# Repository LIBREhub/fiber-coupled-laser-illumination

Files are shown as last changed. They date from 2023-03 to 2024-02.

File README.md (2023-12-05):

# Low-cost and modular fiber-coupled laser illumination for microscopy 

The modular fiber-coupled laser illumination is a free and open-source system that features lasers with various wavelengths coupled in a single optic fiber, enabling easy digital selection without any structural modifications. The system is modular, allowing individual parts to be repurposed and improved in the open-source hardware sense, and easily combined, exchanged, or used on their own.

## Usage

### Instructions

* [Assembly instructions]()
    * [Parts list]()
    * [Firmware installation]()
* Usage instructions
	* [Controller usage]()

This project is documented with GitBuilding - an OpenSource project for documenting hardware projects. For more information on the GitBuilding project, or how
to install GitBuilding please see the [GitBuilding website](http://gitbuilding.io)

## Design files and source code

* [3D printed parts]()
* [Electronics]()
* [Firmware]()

## How do I edit the documentation?

To edit the documentation you do not need to install anything, the documentation files can
be opened in a plain text editor such as Windows Notepad, Notepad++, gedit, VS Code, etc.
We recommend installing GitBuilding to preview any changes to the documentation.
GitBuilding also comes with a browser-based editor that has a live display of the final HTML documentation.

If you have ever used [markdown](https://www.markdownguide.org/basic-syntax/) you will
notice that the files you are editing are markdown files. GitBuilding uses an extended
markdown syntax (that we call BuildUp). This allows you to keep track of parts in the
documentation. More detailed documentation is available on the
[GitBuilding website](https://gitbuilding.io). There is also additional
[syntax for configuration](https://gitbuilding.io/syntax/buildconfsyntax), and for
[part libraries](https://gitbuilding.io/syntax/builduplibrary/).

## Contribute

You're free to fork the project and enhance it. If you have any suggestions to improve it or add any additional functions make a pull-request or [open an issue](https://github.com/LIBREhub/fiber-coupled-laser-illumination/issues/new).
For interactions in our team and with the community applies the [GOSH Code of Conduct](https://openhardware.science/gosh-2017/gosh-code-of-conduct/).

## License

[CERN OHL 2W](LICENSE) © Francisco Martinez, Matías Hurtado-Labarca, Pierre Padilla-Huamantinco, and Vicente Parot. This project is Open Source Hardware - please acknowledge us when using the hardware or sharing modifications.

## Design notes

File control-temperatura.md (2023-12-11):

# Módulo control de temperatura

## Acomplamiento disipador láser con la tapa {pagestep}

Posicionar y acoplar disipador de láser en la tapa sin torcer fibra para evitar daños.

## Acomplamiento ventilador con casing {pagestep}

Posicionar y acoplar el ventilador con disipador en el casing.

## Pegado de cinta térmica {pagestep}

Pegar cinta térmica adhesiva en disipador de láser acoplado en la tapa.

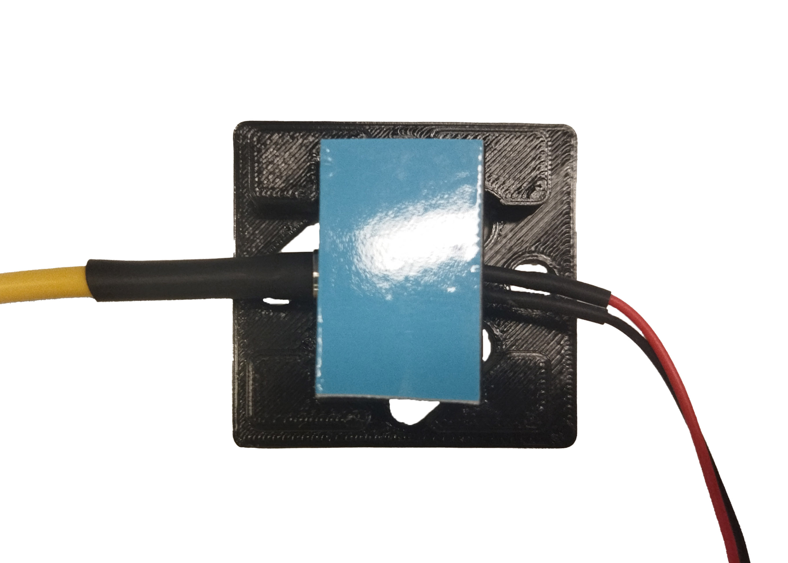
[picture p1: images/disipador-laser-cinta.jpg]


## Ensamblaje final {pagestep}

Desprender capa azul de cinta térmica adherida al disipador del láser.

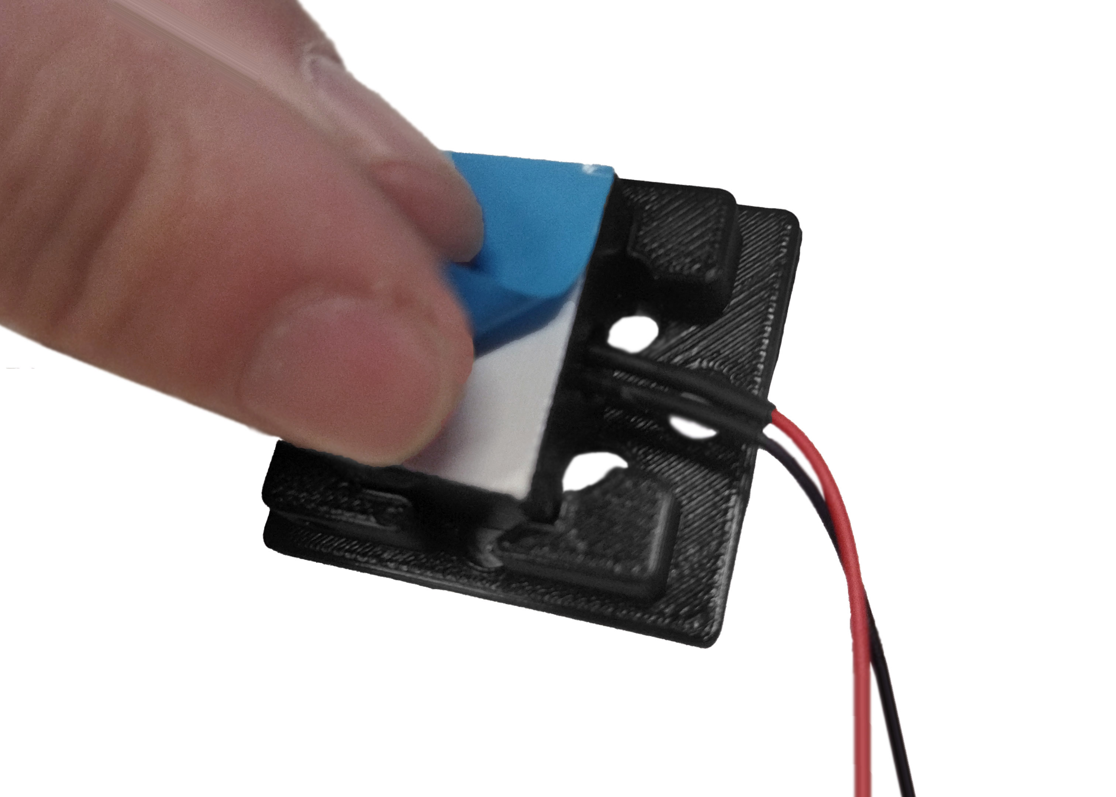
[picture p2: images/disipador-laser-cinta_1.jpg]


Acoplar “Casing Ventilación Láser” (con el ventilador previamente insertado) con “Tapa Ventilación Láser” (disipador y cinta térmica previamente unidos)

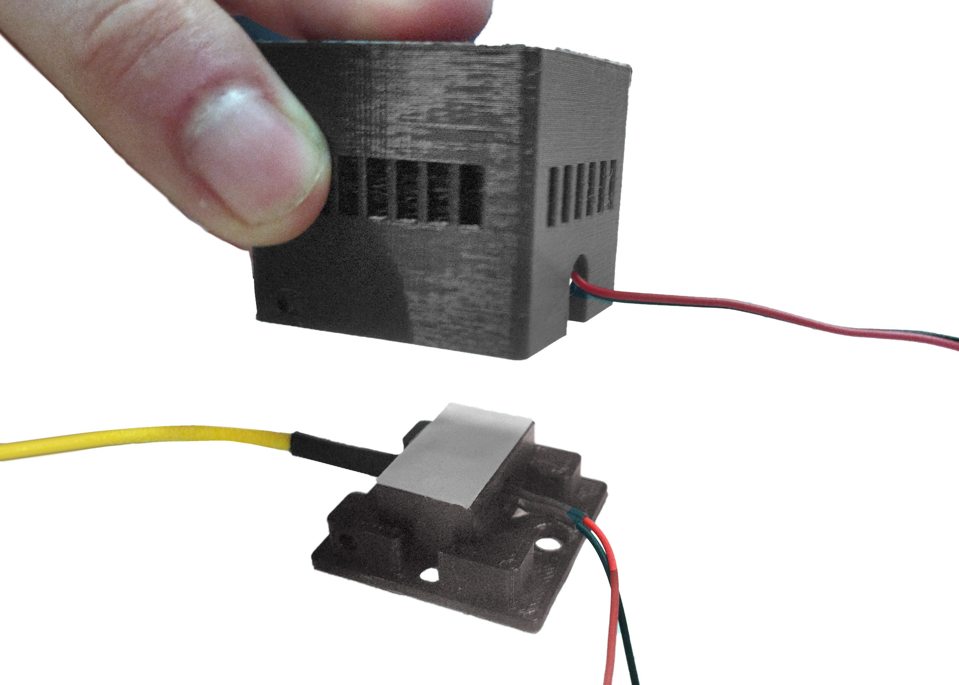
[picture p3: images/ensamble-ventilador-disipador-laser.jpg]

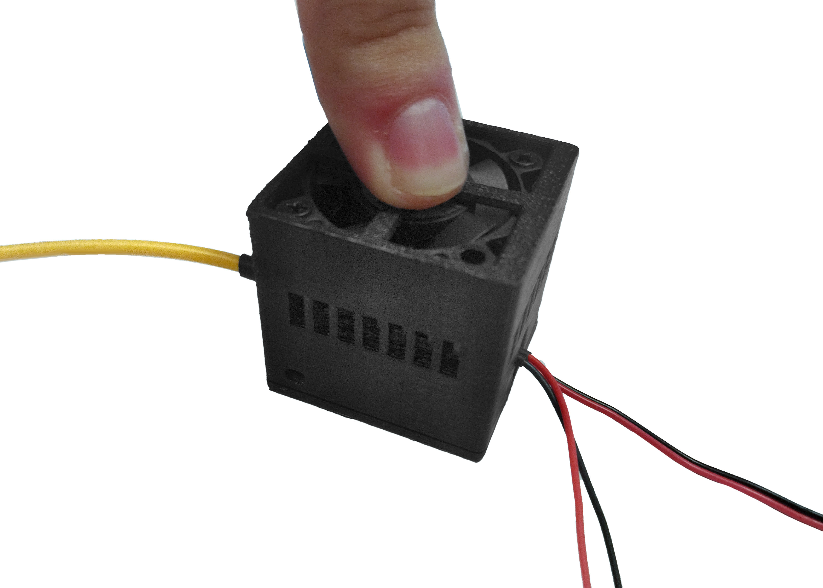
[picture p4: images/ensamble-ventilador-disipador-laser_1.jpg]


Atornillar pernos M3 de 10 mm para fijar ambas partes.

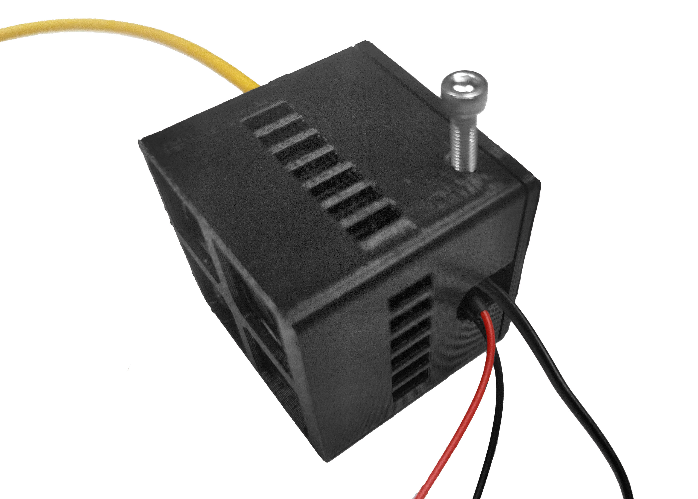
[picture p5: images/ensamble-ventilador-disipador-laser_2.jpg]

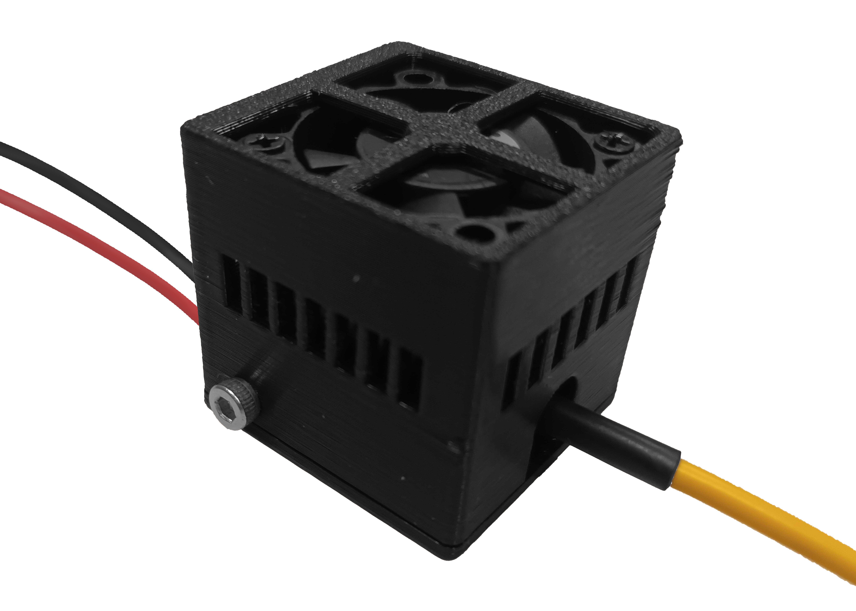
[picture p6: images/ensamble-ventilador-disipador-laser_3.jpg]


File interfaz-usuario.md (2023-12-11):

# Módulo interfaz de usuario

## LM2596 {pagestep}

Posicionar LM2596 tal que la posición del potenciómetro sea la correcta. Atornillar placa a la tapa TOP usando llave allen M3.




## Interruptores {pagestep}

Introducir señuelo de carga (tarjeta electrónica morada) a través de la perforación para el interruptor del motor. 





Introducir el segundo interruptor a través de la perforación para el láser y presionar para fijar al panel (tapa TOP).

## Señuelo de carga {pagestep}

Alinear la tarjeta electrónica morada con el adaptador como se muestra a continuación.



Atornillar pernos M2 para fijar tarjeta electrónica.




Insertar tuercas M3 y posteriormente fijar al panel (tapa TOP).




## Fijación de cable adaptador M12 {pagestep}

Introducir cable M12 desde el interior de la tapa TOP en su respectiva perforación. Posteriormente fijar la tuerca M12.


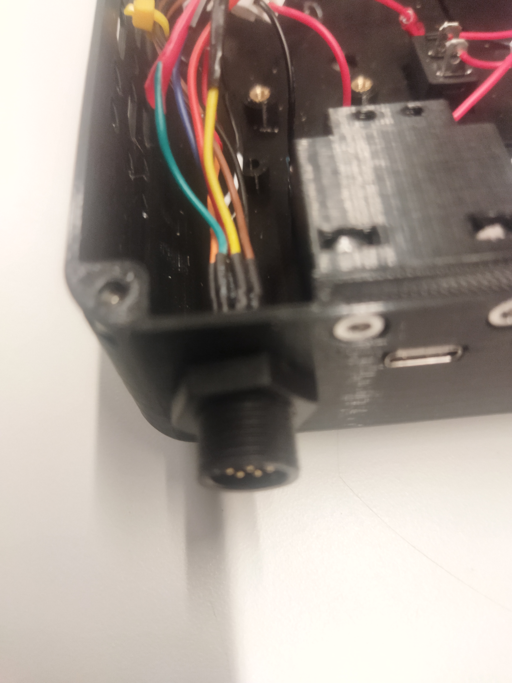
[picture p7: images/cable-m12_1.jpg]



## Amperímetro {pagestep}

Introducir y presionar amperímetro en el panel (tapa TOP).  Fijar amperímetro con tuercas M3.




## Fijación de tarjeta electrónica {pagestep}

Posicionar y fijar tarjeta electrónica en panel (tapa TOP) usando 4 tornillos incluidos. Respetar orientación acorde a las siguientes imágenes.


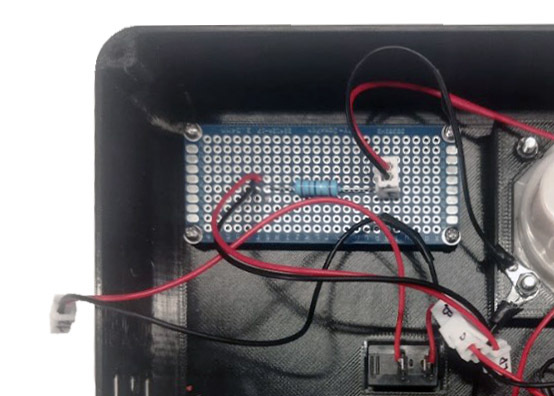
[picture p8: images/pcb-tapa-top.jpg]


## Conexión de cables {pagestep}

Conectar cables A, B, C y D en la misma letra según corresponda. Conectar golillas K1 y K2 en las posiciones señaladas en amperimetro. Conectar golillas color negro en el mismo perno del amperimetro según como se indica en las siguientes imágenes.

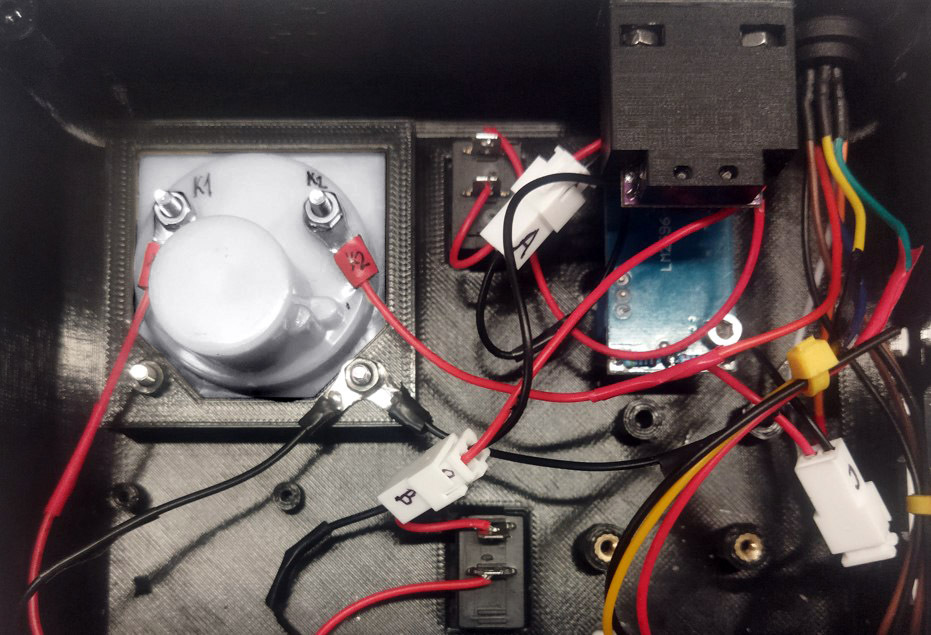
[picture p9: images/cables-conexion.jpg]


Para la conexión de las golillas utilizar tuercas M3. 

## Conexión y fijación del driver de láser {pagestep}

Conectar cables LD, 12, FAN a tarjeta Laser Driver en puertos de láser, alimentación de 12 V y ventilador respectivamente.





Voltear tarjeta de laser driver orientándola tal que el potenciómetro quede bien posicionado. Ensamblar separadores con pernos M3 para fijar tarjeta.





## Montaje de tapa acrílica {pagestep}

Posicionar 4 tuercas M3 como se muestra en la siguiente imagen.

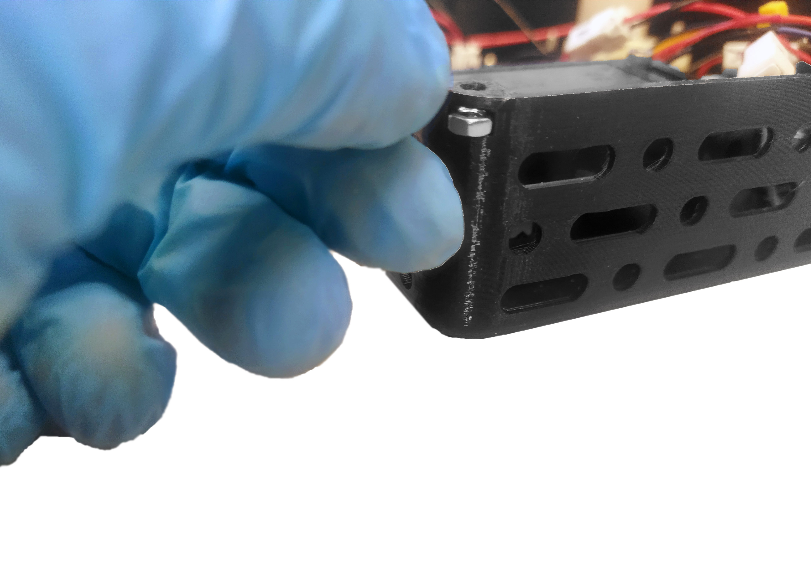
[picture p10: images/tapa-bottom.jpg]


Orientar tapa BOTTOM de acrílico como se muestra en la siguiente imagen. Apretar pernos M3 y posteriormente pegar gomas antideslizantes en cada perno.



## Ensamblaje de perillas {pagestep}

Posicionar y presionar cada perilla en cada orificio de la tapa TOP.




La interfaz de usuario ensamblada debe verse como en las siguientes imágenes.




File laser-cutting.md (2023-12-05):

# Laser cut the acrylic parts

{{BOM}}

[Acrylic sheet]: parts/materials/acrylic-sheet.md "{cat:material}"
[Laser cutting machine]: parts/tools/laser-cutting-machine.md "{cat:tool}"

## Set your laser cutting machine settings {pagestep}

Laser-cutting acrylics is relatively simple. The basic steps for achieving good-quality cut acrylic parts are listed [here].

Settings for laser cutting acrylics will vary according to the machine. The table below lists the settings we used: 

|Setting     |Value        |
|------------|--           |
|Material    |Acrylic 3mm |
|Power (W)   |40 |
|Speed (mm/s)|20 |

We recommend testing the parameters for acrylic laser cutting using a test matrix. Download and laser cut the [test matrix](parts/materials/test-matrix.md) file. This will only use about an 8x9x0.5cm acrylic sheet.

The result should look like this:

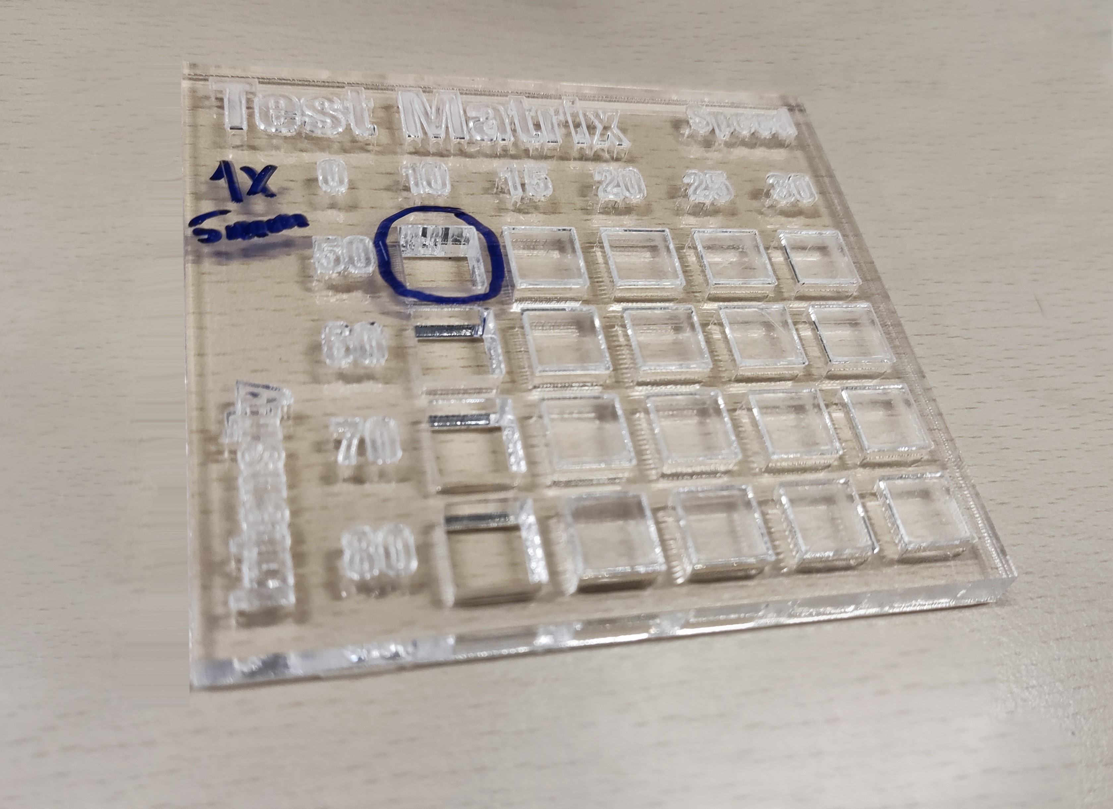
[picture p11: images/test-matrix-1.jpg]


## Laser cutting {pagestep}

Now you have tested your [laser cutting machine][Laser cutting machine]{qty: 1} and [acrylic sheet][Acrylic sheet]{Qty: 1} you can laser cut the following parts:

### Remove film

* If there is protective film on the acrylic, remove it now.

* Your plates are now prepared and ready to use.

[guide to tapping acrylic]: http://www.ultimatehandyman.co.uk/how-to/acrylic/tapping-acrylic
[here]: https://www.xometry.com/resources/sheet/about-laser-cutting-acrylic/

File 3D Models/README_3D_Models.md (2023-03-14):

# 3D Models
## List of Contents
1. Driver Mounting Plate
   - **A:** Used for two drivers model [INSERT MODEL]
   - **B:** Used for one driver model [INSERT MODEL A] and one driver model [INSERT MODEL B] 
2. Power Supply Mounting Plate
3. Single Fiber Tray 
4. Double Fiber Tray

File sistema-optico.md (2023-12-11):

# Módulo óptico

>! **Cuidado** Utilizar guantes de nitrilo para la manipulación de todas las piezas del módulo óptico. *Tener especial cuidado con los lentes y la fibra láser.*

## Lente óptico {pagestep}

Calzar anillo interno 1 en herramienta OP. Luego, introducir en tubo óptico y girar hasta una profundidad de 6mm.

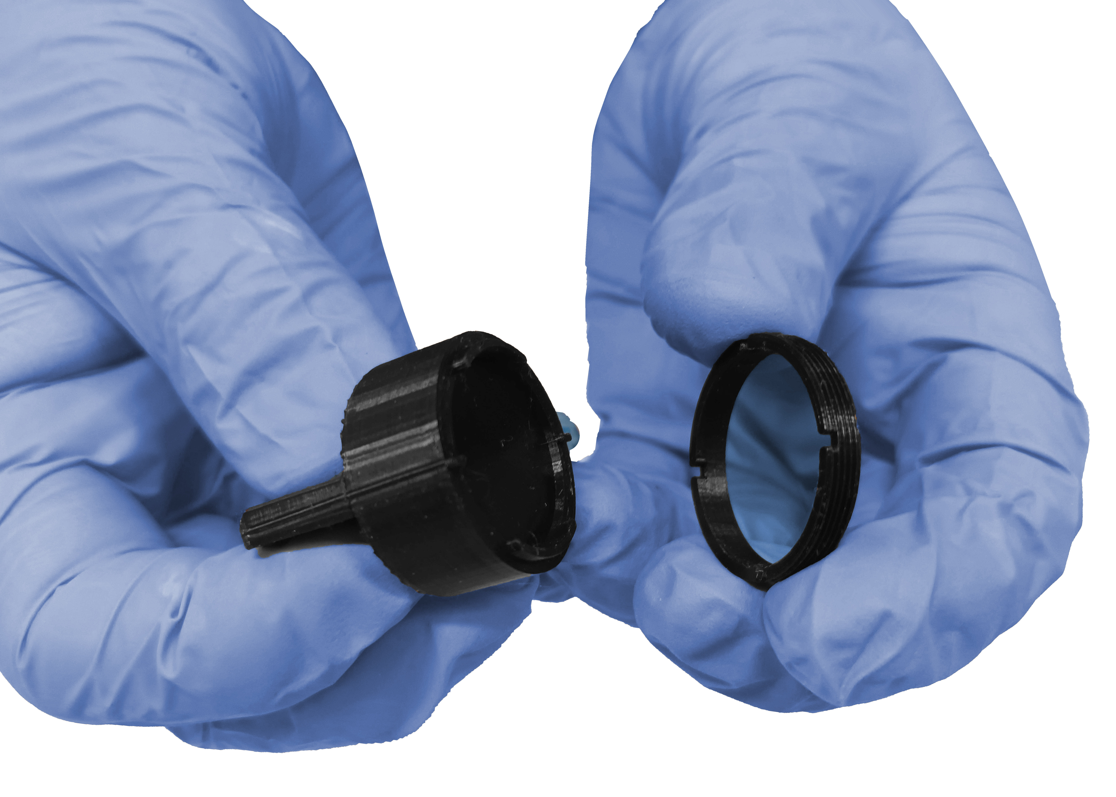
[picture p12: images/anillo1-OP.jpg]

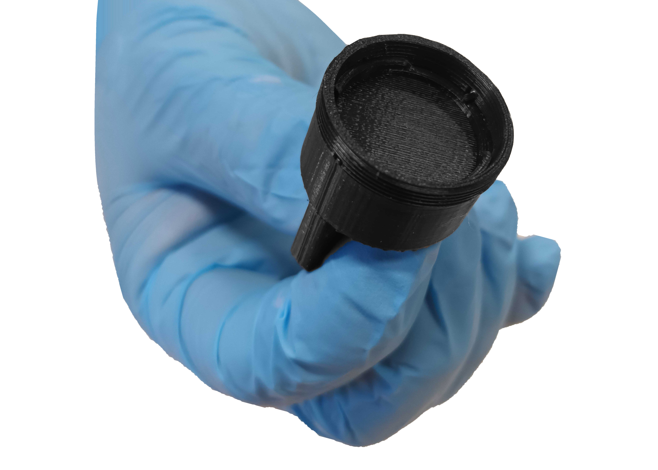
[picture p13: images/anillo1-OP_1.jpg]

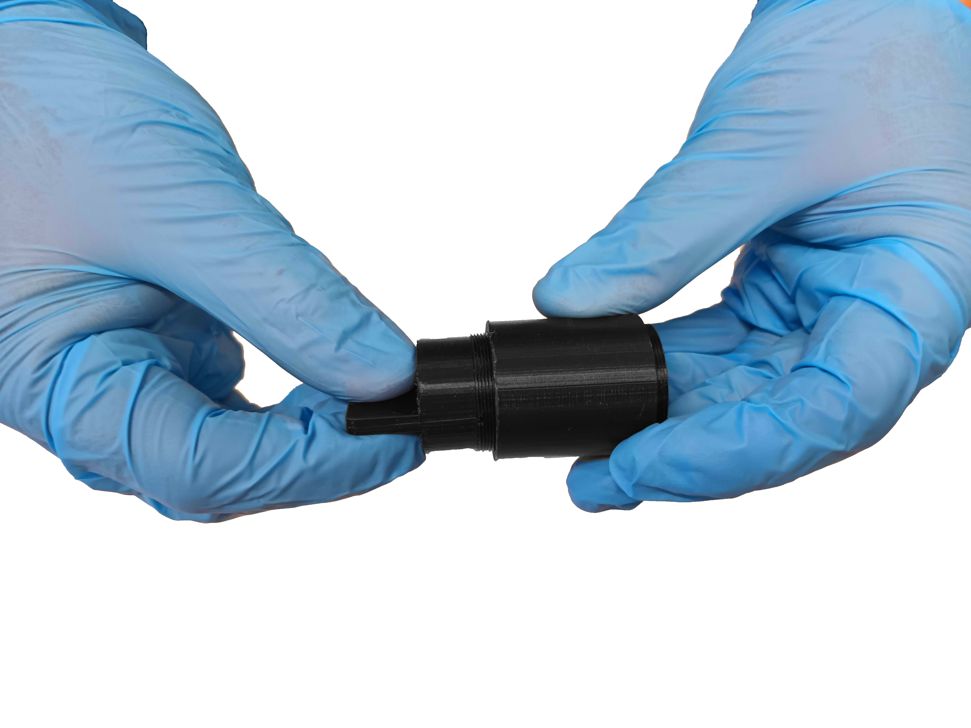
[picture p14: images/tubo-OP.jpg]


Insertar lente en tubo óptico.

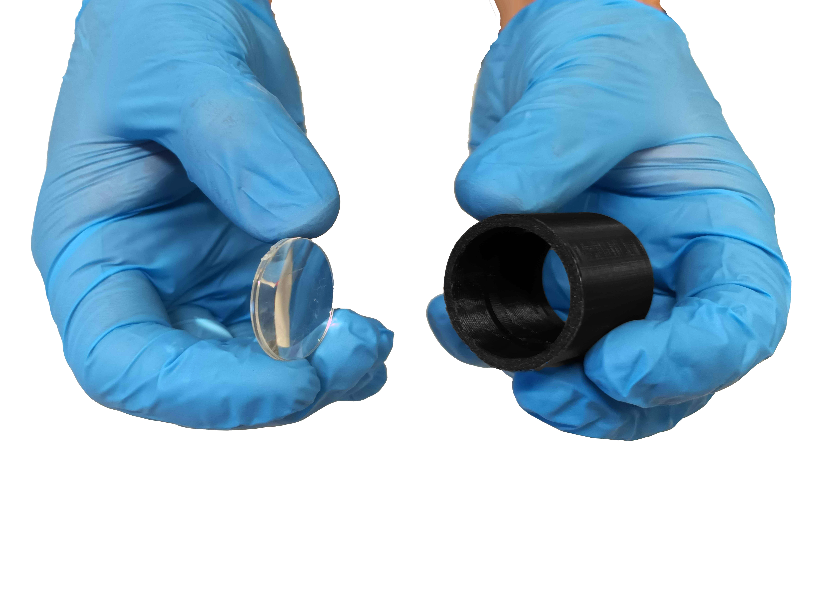
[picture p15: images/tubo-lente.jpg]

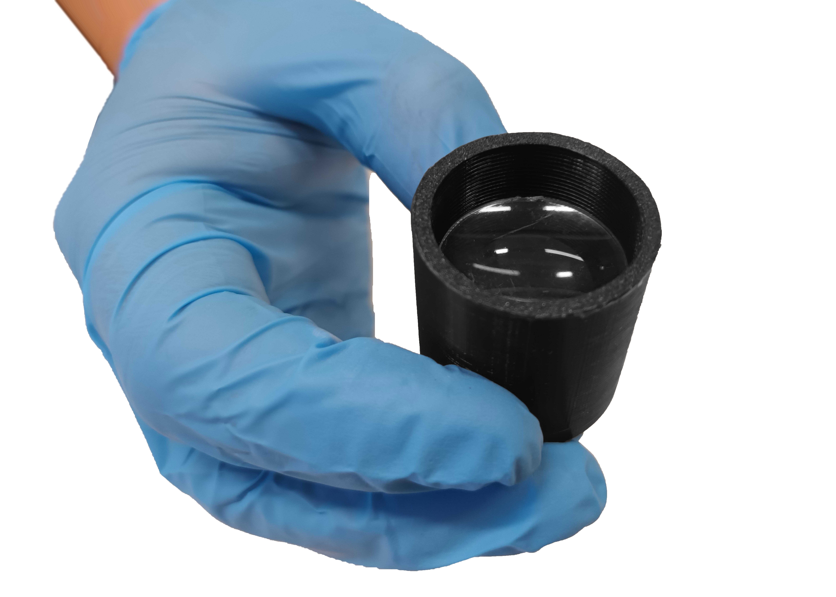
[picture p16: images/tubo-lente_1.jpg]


Calzar anillo interno 2 en herramienta OP, introducir en tubo óptico y girar hasta el tope.

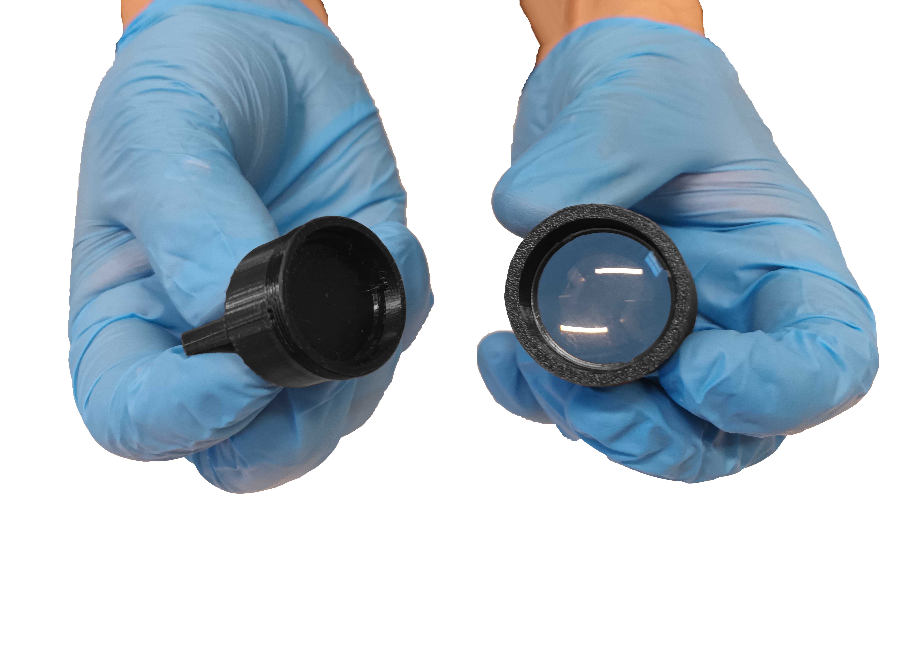
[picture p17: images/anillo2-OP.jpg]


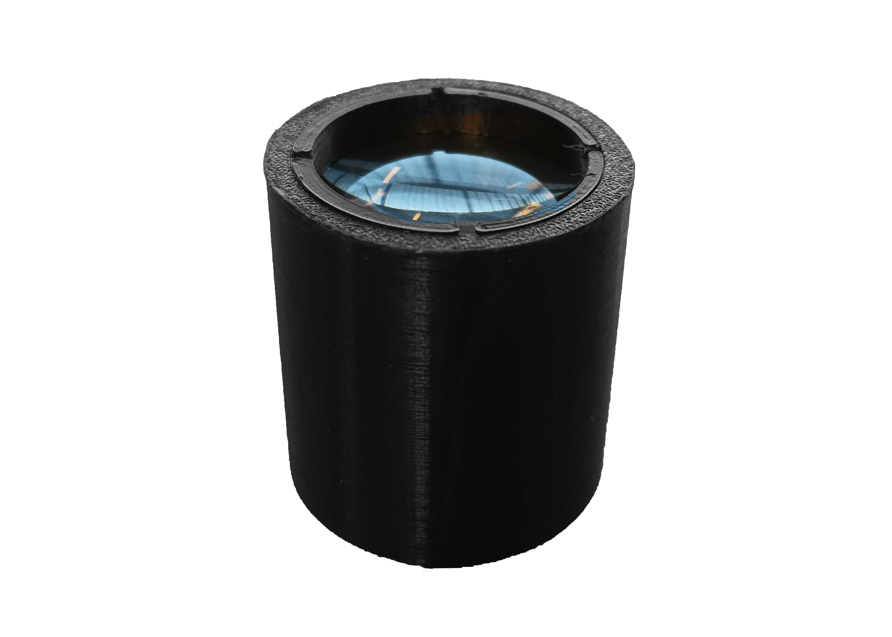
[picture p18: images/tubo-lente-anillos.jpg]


## Tubos ópticos {pagestep}

Para este paso, debe disponer del tubo óptico con su lente acoplado, ensamblado en el paso anterior.

Calzar ambos tubos y girar hasta el final. 

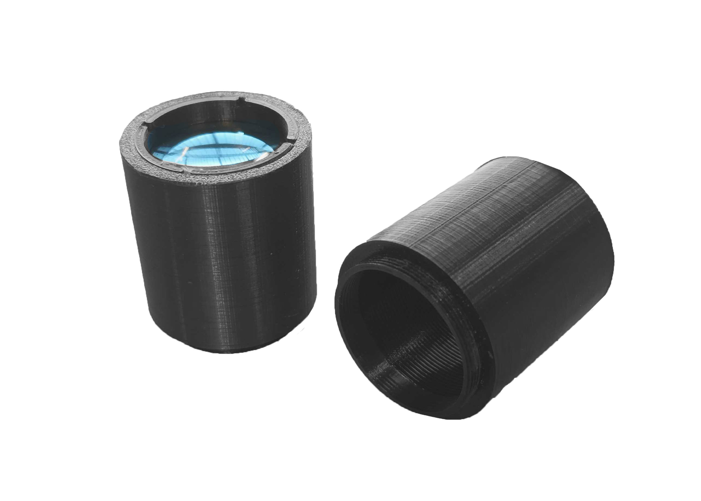
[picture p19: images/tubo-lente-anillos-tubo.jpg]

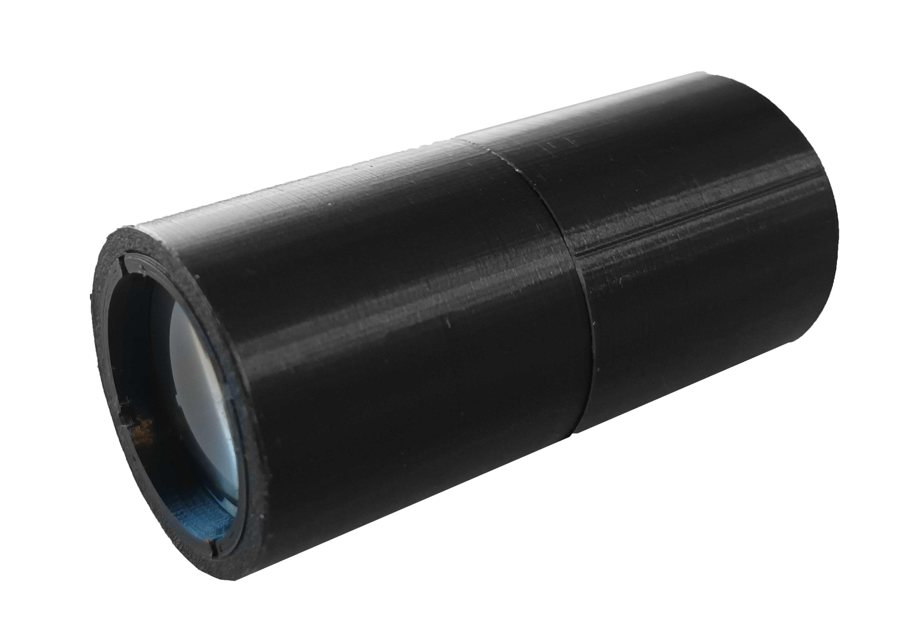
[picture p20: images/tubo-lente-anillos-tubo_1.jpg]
  

## Base {pagestep}

Para este paso, debe disponer del tubo óptico extendido, ensamblado en el paso anterior.

Poner abrazaderas en superficie horizontal a una distancia de 25 mm entre ambas partes. Luego, ensamblar tubo óptico a ambas abrazaderas presionando hacia abajo.

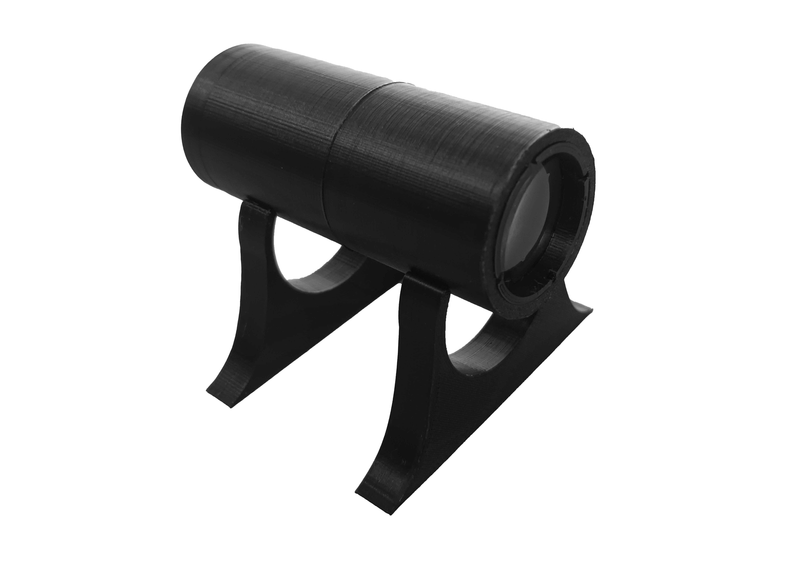
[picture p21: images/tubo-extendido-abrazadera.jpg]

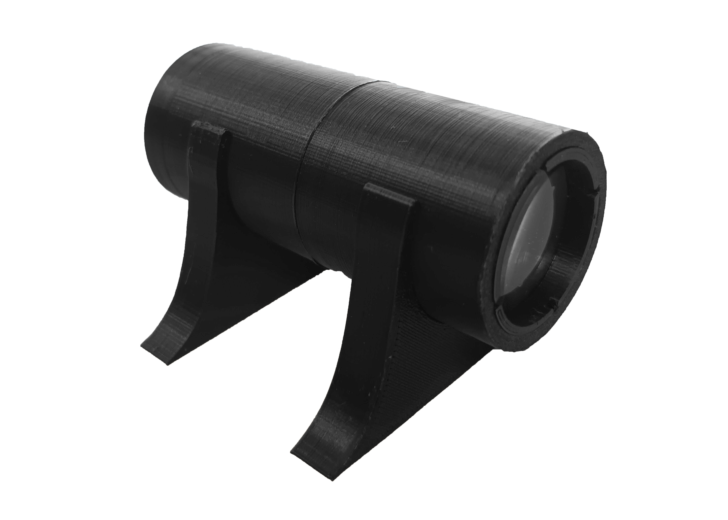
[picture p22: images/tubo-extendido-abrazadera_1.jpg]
  

## Adaptador de fibra láser {pagestep}

Para este paso, debe disponer del tubo óptico extendido con las abrazaderas, ensamblado en el paso anterior.

Calzar adaptador de fibra láser y girar hasta el final.

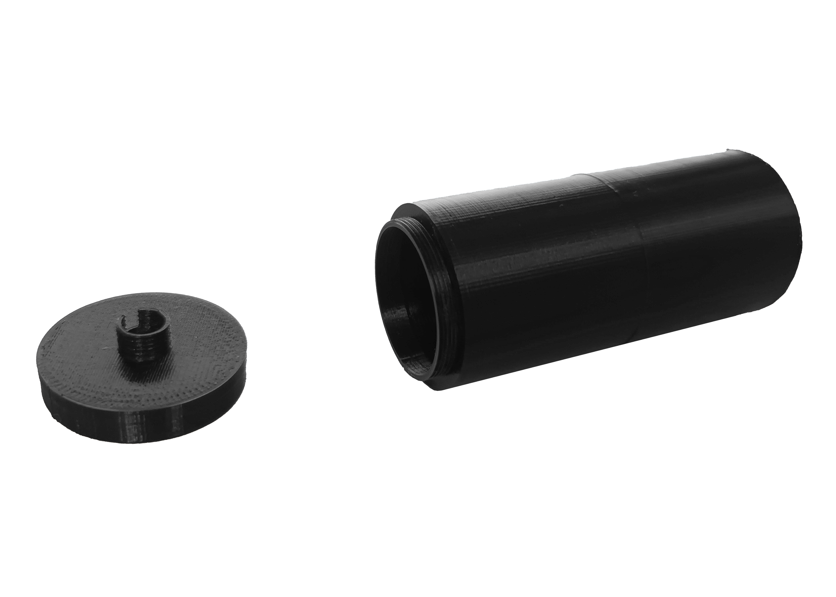
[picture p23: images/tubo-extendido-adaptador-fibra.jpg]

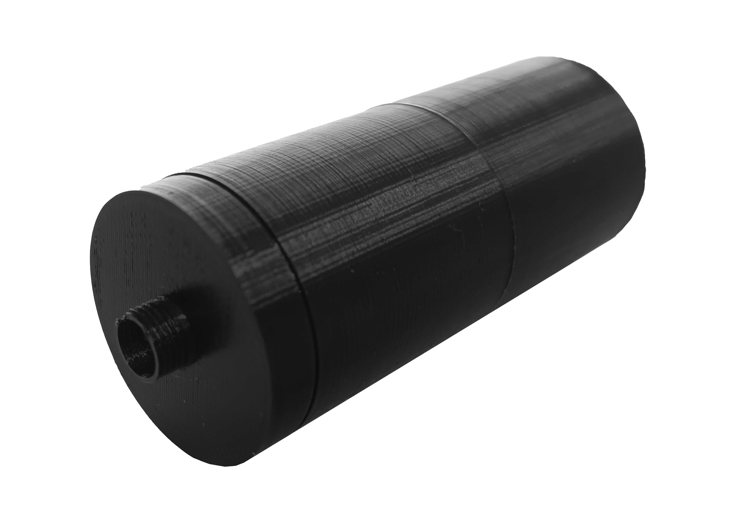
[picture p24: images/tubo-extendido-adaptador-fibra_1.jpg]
  

Retirar tapa de láser, ensamblar láser con adaptador de fibra láser y girar adaptador láser hasta el final.

>! **Cuidado** No tocar fibra óptica. Manipular componentes como se muestra en las imágenes.


  



El ensamblaje debe verse como en la imagen inferior.



## Difusor {pagestep}

Calzar difusor en herramienta OP e introducir en tubo óptico. Girar hasta el final del tubo.




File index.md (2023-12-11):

# Modular fiber-coupled laser illumination

El sistema modular de iluminación láser acoplada a fibra es un dispositivo libre y de fuente abierta. Este sistema puede utilizar láseres con varias longitudes de onda, acopladas en una sola fibra óptica, lo que permite una fácil selección digital sin modificaciones estructurales. Su diseño modular permite reutilizar y mejorar piezas individuales, combinarlas, intercambiarlas o utilizarlas fácilmente por sí solas.

>i **Nota:** Este sistema esta basado en algunos recursos de la plataforma [SQUID](https://github.com/prakashlab/squid-tracking).

Para aprender más sobre este sistema y otras tecnologías libres para bioimágenes, te invitamos a visitar la [página web de LIBRE hub](https://librehub.github.io/).

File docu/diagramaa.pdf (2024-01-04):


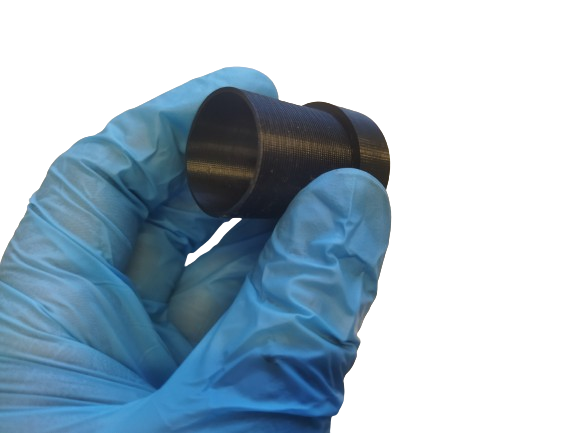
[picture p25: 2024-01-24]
images/tubolente2.png

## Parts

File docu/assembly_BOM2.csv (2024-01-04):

Name in documentation | Category | Qty | Link | Notes
Motor vibrador | hardware | 1 | MTSPACE 10pcs/Set 4x8mm DC 1.5-3V Micro Cell Phone Coreless Vibration Motor Vibrator Mini Massage Motor for SANYO High Quality - AliExpress | 4x8 mm
Señuelo de Carga | hardware | 1 | https://es.aliexpress.com/item/1005004996088932.html?src=google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
Cargador USB-C | hardware | 1 | https://es.aliexpress.com/item/1005005984443043.html?src=google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
Cinta adhesiva térmica | hardware | 1 | https://es.aliexpress.com/item/4000233593859.html?src=google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 | Heat Sink Dimensionsions: 15x24mm
Interruptor basculante | hardware | 2 | http://aliexpress.com/item/1005003838211957.html
LM2596 | hardware | 1 | https://es.aliexpress.com/item/32952599622.html?curPageLogUid=km7nIVWql5cD
cable conector macho 2.54mm 2P | hardware | 3 | http://aliexpress.com/item/33015429167.html
cable conector hembra 2.54mm 2P | hardware | 4 | http://aliexpress.com/item/33015429167.html | en caso de incluir circuito limitador de corriente adquirir una unidad adicional
cable conector macho 2.54mm 3P | hardware | 1 | http://aliexpress.com/item/33015429167.html | ventilador laser driver 500mA
cable conector macho 2mm, 2P | hardware | 1 | http://aliexpress.com/item/1005001649158434.html | ventilador laser driver 4A
Terminales RV2-3 | hardware | 1 | https://es.aliexpress.com/item/1005004290771619.html?src=google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 | uso opcional: para ajustar cables en amperimetro
Panel M12 y Cable conector 8 pines | hardware | 1 | https://es.aliexpress.com/item/1005005922136440.html?gatewayAdapt=glo2esp | 2 pines para + y - del láser, 2 pines para el motor, 2 pines para el ventilador (podria usarse uno de 6 pines)
Ventilador con disipador 30mm 12V | hardware | 1 | https://a.aliexpress.com/_msGmWnW
PCB para soldar 3x7cm | hardware | 1 | https://es.aliexpress.com/item/1005004818919331.html?scm_id=1007.40000.327270.0&scm-url=1007.40000.327270.0 | para soldar circuito limitador de corriente
LM317 | hardware | 1 | https://es.aliexpress.com/item/1005005777401817.html?curPageLogUid=VpS7hg2IFfcP
Disipador LM317 | hardware | 1 | http://aliexpress.com/item/4000004835894.html
Pernos disipador TO220 | hardware | 1 | https://es.aliexpress.com/item/1005002838348039.html?src=google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
2 Ohm, 1W | hardware | 1 | http://aliexpress.com/item/1005002788900288.html
Resistencias | hardware | 1 | Resistencia de película metálica 100, 1/4W, 1R ~ 22M, 100R, 220R, 1K, 1% K, 1,5 K, 2,2 K, 10K, 22K, 47K, 4,7 K, 100, 100, 1K5, 2K2, 4K7 ohm, 220 unidades/lote - AliExpress | 470 ohm, 150 ohm, 1/4 W
Amperimetro | hardware | 1 | http://aliexpress.com/item/1005005867205046.html | 500mA o 1A dependiendo la fuente de corriente y láser a usar
Fiber coupling diode laser | hardware | 1 | Shenzhen Guangchuangfeng Technology Co., Ltd | 408 nm/300mW, 488nm/55mw, 638nm/700mW
Adjustable Laser Diode Driver with TTL | hardware | 1 | 0-500mA Adjustable Green/Bule Laser Diode Constant Current Driver with TTL_LD Constant Current Driver_Drivers_Shenzhen Micost-optotech Co., Ltd | 500mA, 4A
Lente 1 pulgada | hardware | 2 | http://aliexpress.com/item/32685561574.html | 45mm distancia focal

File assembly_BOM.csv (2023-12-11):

Name in documentation | Category | Qty | Full Name | Notes

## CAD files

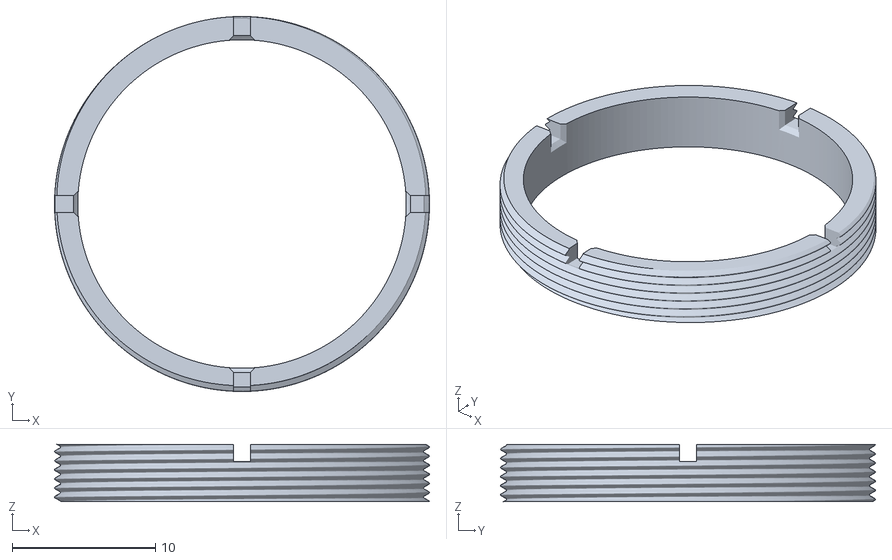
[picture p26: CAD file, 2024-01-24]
models/anillo-TL.stl
26.2 x 26.2 x 4.00

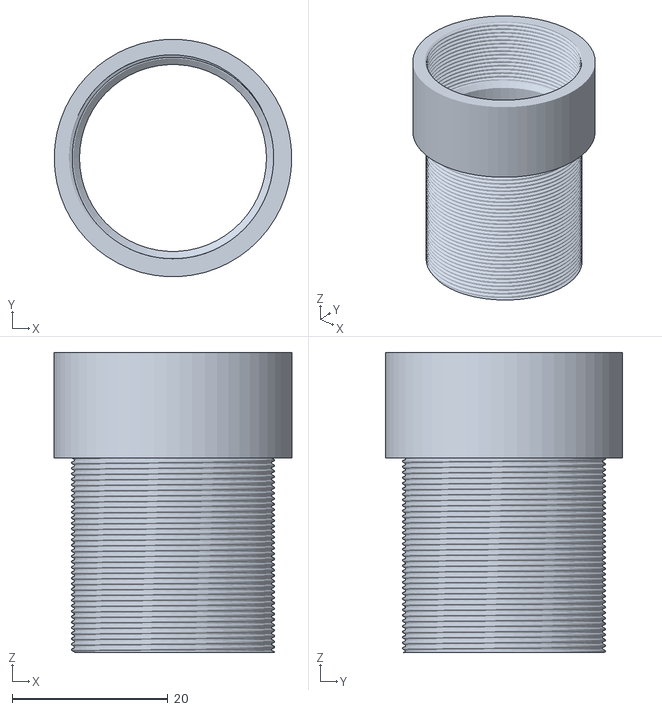
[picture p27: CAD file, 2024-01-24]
models/Tubolente.stl
30.5 x 30.5 x 38.5

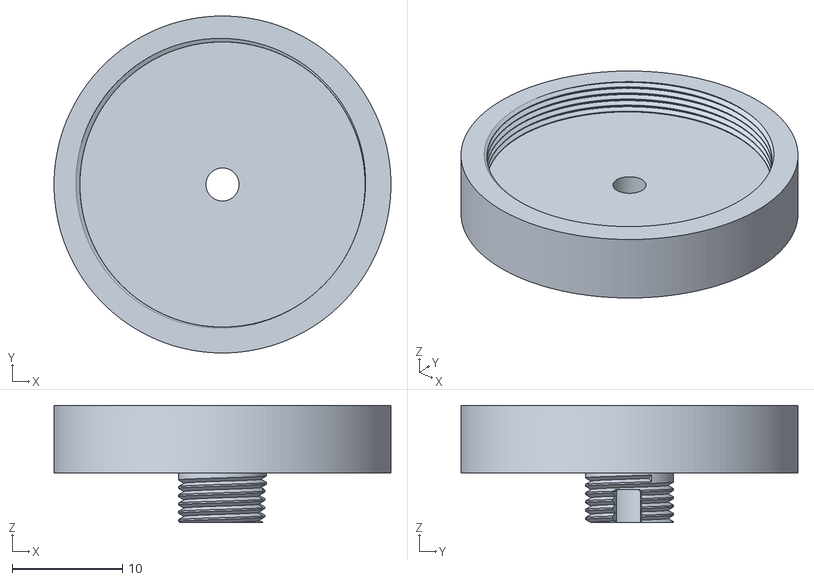
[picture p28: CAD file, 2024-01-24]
models/adaptadorfibra-TL.stl
30.5 x 30.5 x 10.6

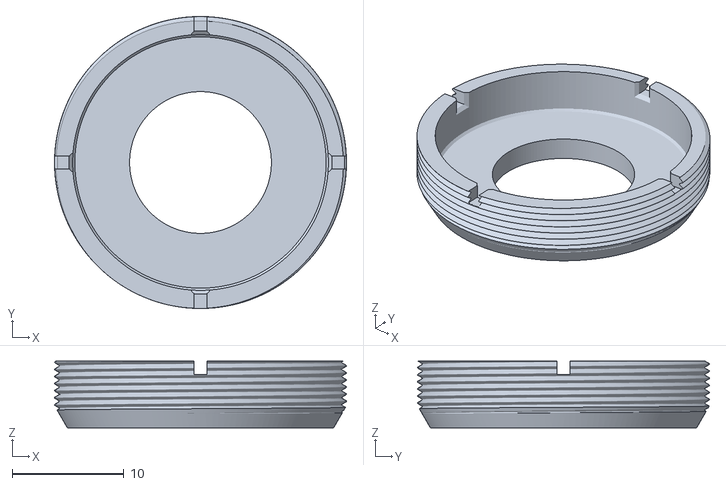
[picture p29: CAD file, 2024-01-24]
models/difusor-TL.stl
26.2 x 26.2 x 6.00

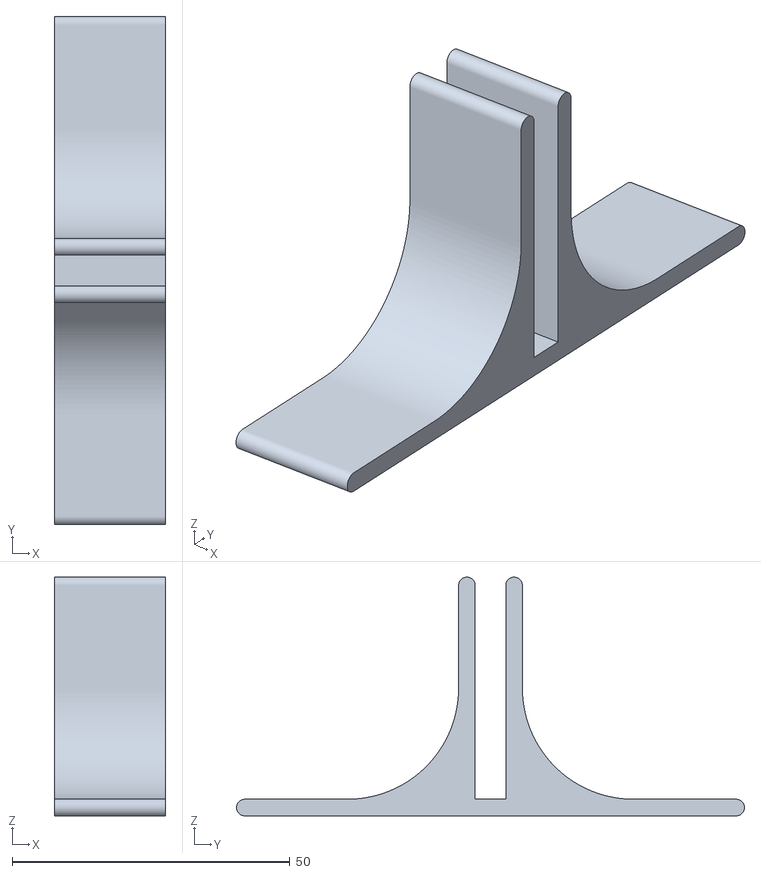
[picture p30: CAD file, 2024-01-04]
models/sujetador.stl
20.0 x 91.5 x 43.0

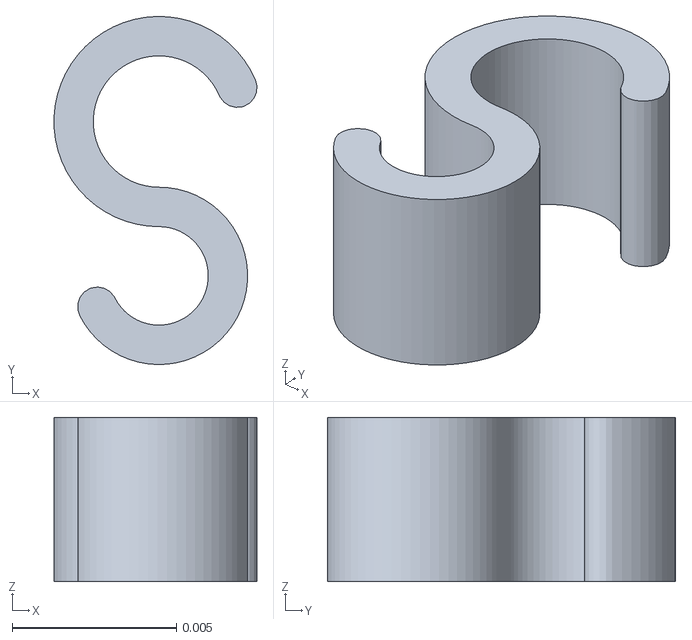
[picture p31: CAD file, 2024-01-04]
models/sujetadorm.stl
0.00618 x 0.0106 x 0.005

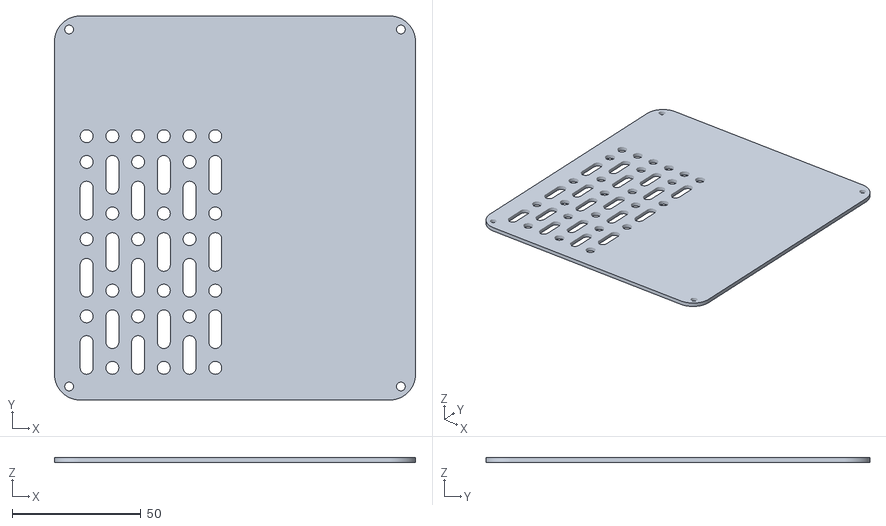
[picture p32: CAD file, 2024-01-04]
models/acrilico.stl
140.3 x 149.2 x 2.00

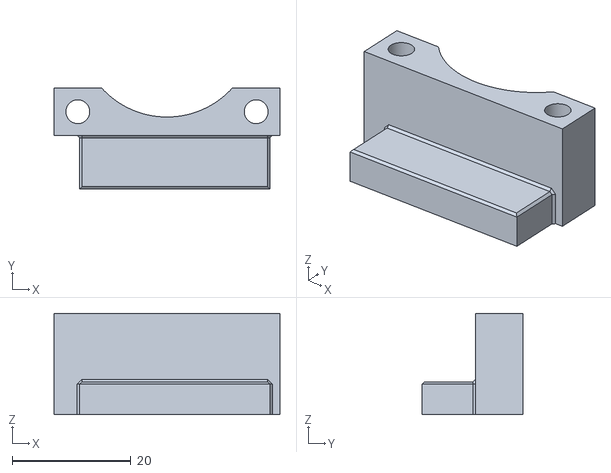
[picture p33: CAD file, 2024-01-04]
models/S5.stl
38.0 x 17.0 x 17.0

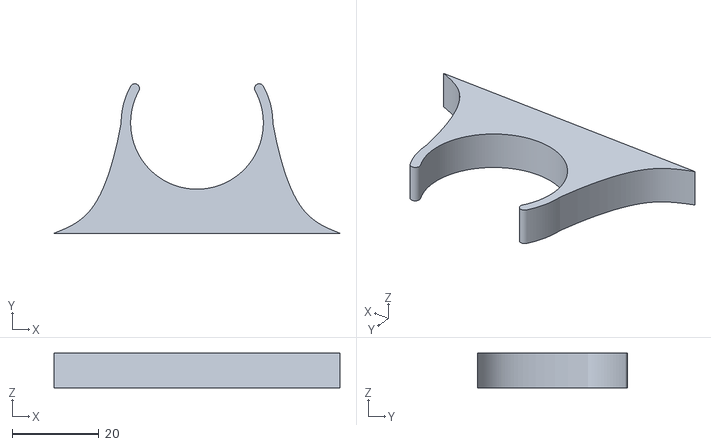
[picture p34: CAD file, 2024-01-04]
models/abrazadera.stl
66.0 x 34.5 x 8.00

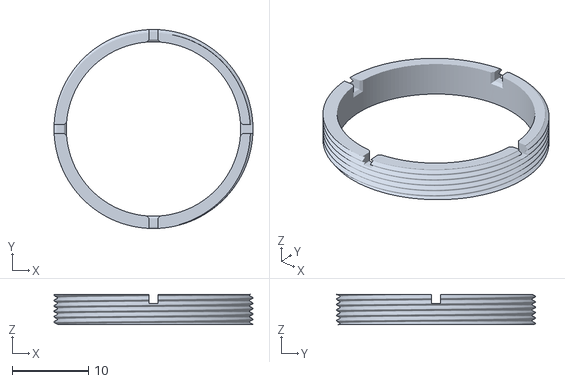
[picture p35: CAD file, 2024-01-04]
models/anillo.stl
26.2 x 26.2 x 4.00

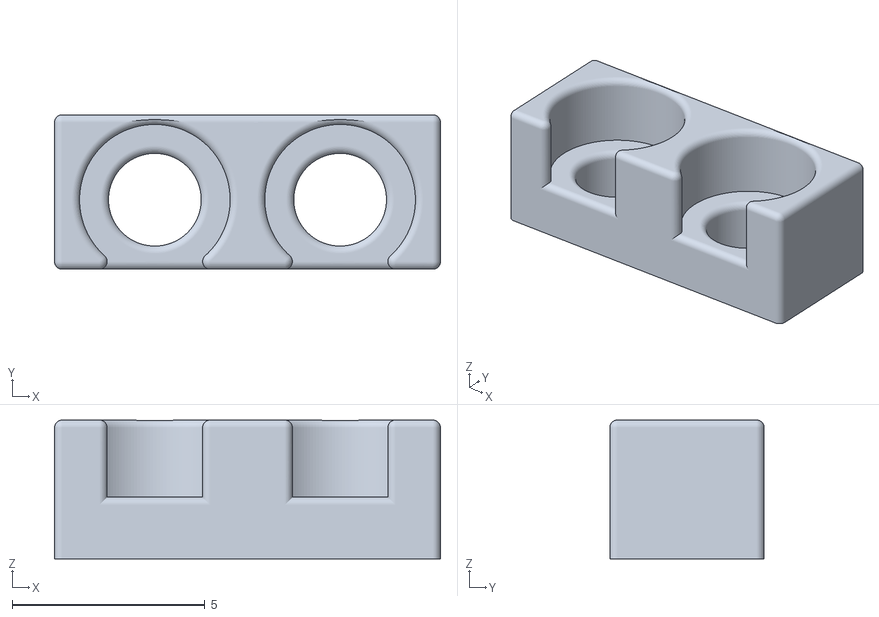
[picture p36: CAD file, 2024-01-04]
models/AdapterM2.stl
10.0 x 4.00 x 3.60

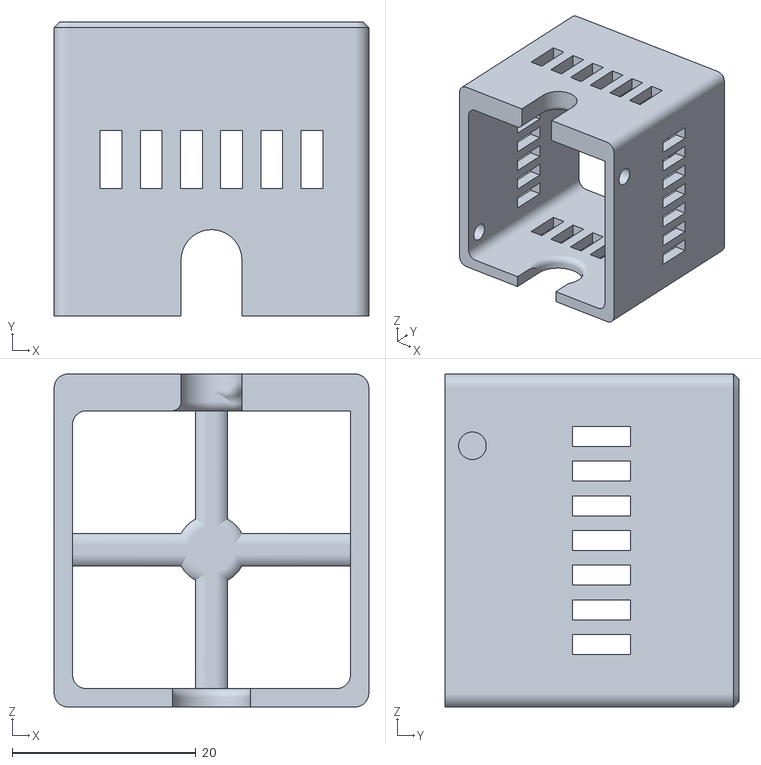
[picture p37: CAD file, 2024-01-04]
models/ventiladort.stl
34.2 x 32.0 x 36.2

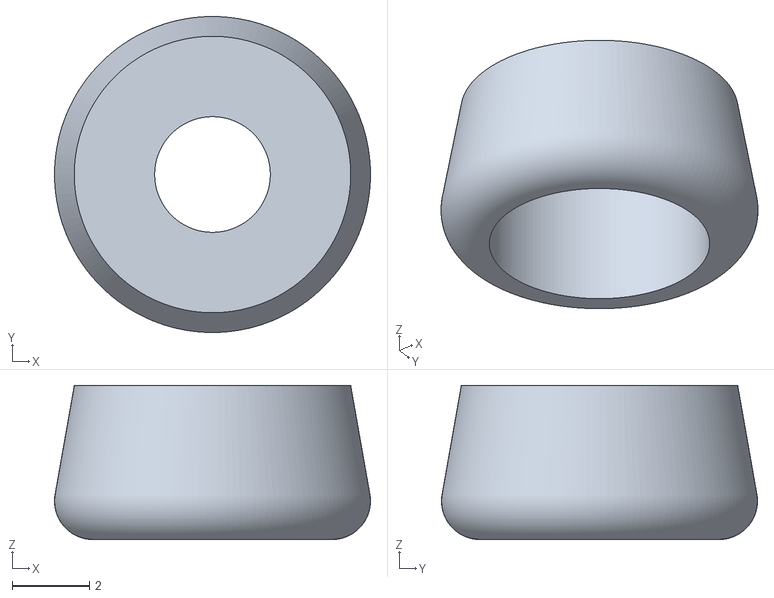
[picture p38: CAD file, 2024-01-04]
models/patabase.stl
8.20 x 8.20 x 4.00

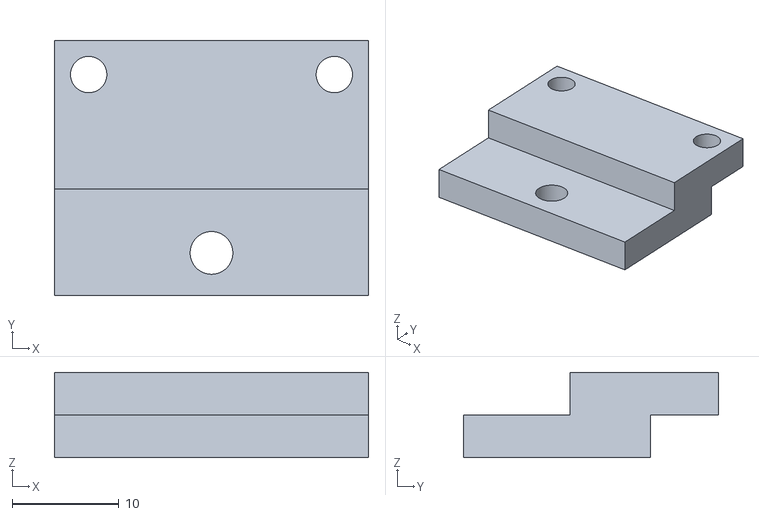
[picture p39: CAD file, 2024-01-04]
models/S2.stl
29.4 x 23.9 x 8.00

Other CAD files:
models/Difusor.stl
models/ventiladorb.stl
models/Herramienta.stl
models/S3.stl
3D Models/1-Driver_Mounting_Plate_A.ipt
3D Models/1-Driver_Mounting_Plate_B.ipt
3D Models/2-PowerSupply_Mounting_Plate.ipt
models/S1.stl
models/S4.stl
models/adaptadorfibra.stl
models/adaptadorusb.stl
models/leg_test.stl
models/manillac.stl
models/manillal.stl

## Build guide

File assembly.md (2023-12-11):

# Modular fiber-coupled laser illumination

Antes de iniciar con la construcción de este sistema de iluminación, usted deberá conseguir todos los componentes que aparecen en esta [lista de materiales]{BOM}.

## Instrucciones

Estas instrucciones lo guiarán en cómo ensamblar el sistema modular de iluminación láser acoplada a fibra.

Para acceder a las instrucciones, tiene los siguientes formatos: [Google Drive](https://docs.google.com/document/d/16imha3nkvypMGve5x3KE3pPr4JS-nB1yEqmpo9TT694/edit?usp=sharing) y [PDF](docu/assembly_instructions.pdf). 

Este sitio web esta basado en la plataforma GitBuilding. El ensamblaje está detallado en los siguientes pasos:

* [.](sistema-optico.md){step}
* [.](control-temperatura.md){step}
* [.](interfaz-usuario.md){step}

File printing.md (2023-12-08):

# Print the plastic parts

{{BOM}}

[PLA filament]: parts/materials/pla_filament.md "{cat:material}"
[RepRap-style printer]: parts/tools/rep-rap.md "{cat:tool}"
[Precision wire cutter]: parts/tools/precision-wire-cutters.md "{cat:tool}"
[Utility knife]: parts/tools/utility-knife.md "{cat:tool}"
[leg test]:models/leg_test.stl "{previewpage}"

## Set your printer settings {pagestep}

Almost all station parts can be printed out of [PLA filament] on most [RepRap-style printers][RepRap-style printer]{qty:1}.

We recommend the following printer settings:

|Setting        |Value          |
|------------   |--             |
|Material       |PLA            |
|Material Colour       |Black            |
|Material Temperature |Recommended by the PLA brand|
|Layer height   |0.2mm or less  |
|Infill         |Printer default or more|
|Brim           |Recommended for all parts|
|Slice gap closing radius |0.001mm |

Test whether your printer can print the pieces for this station or other open-source designs. Download and print the [leg test] file. This will only use about [5 grams of PLA][PLA filament].

The result should look like this (this has been printed with a brim):

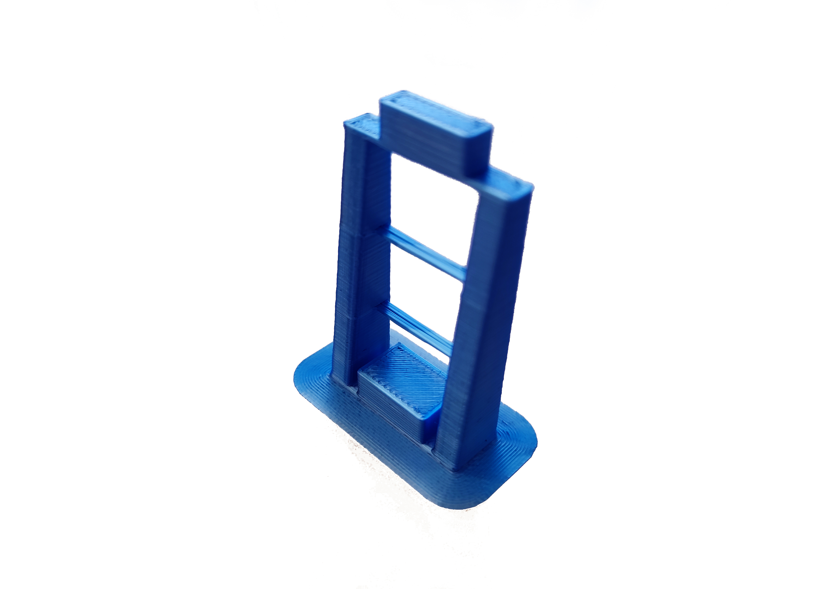
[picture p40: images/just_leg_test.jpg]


As a general rule, strength is more important than surface finish, so very thin layers (less than 0.15mm or so) are unlikely to result in a station that performs any better, though it may improve the appearance.

## Printing {pagestep}

Now you have tested your [3D printer][RepRap-style printer] and [filament][PLA filament]{qty:200gr} you can print the following parts:

You can download all the STLs as a single zipfile.

## Clean-up of printed parts {pagestep}

>!! **Be careful when removing brim:** To avoid injury, first remove the bulk of the brim without a knife. Remove the remaining brim with a peeling action as described below.

Carefully remove the printing brim from all parts. To remove brim:

1. Use [precision wire cutters][Precision wire cutter]{qty: 1} to remove most of the brim from the part.
2. Clean up the remaining brim with a [utility knife][Utility knife]{qty: 1, note: "Not a scalpel!"}:
    * Hold the knife in your dominant hand with 4 fingers curled around the handle, leaving your thumb free.
    * Hold the part in your other hand, as far away from the surface, to be cut as possible.
    * Support the part with the thumb of your dominant hand.
    * Place the blade on the surface to be cut, and carefully close your dominant hand, moving the blade, under control, towards your thumb.

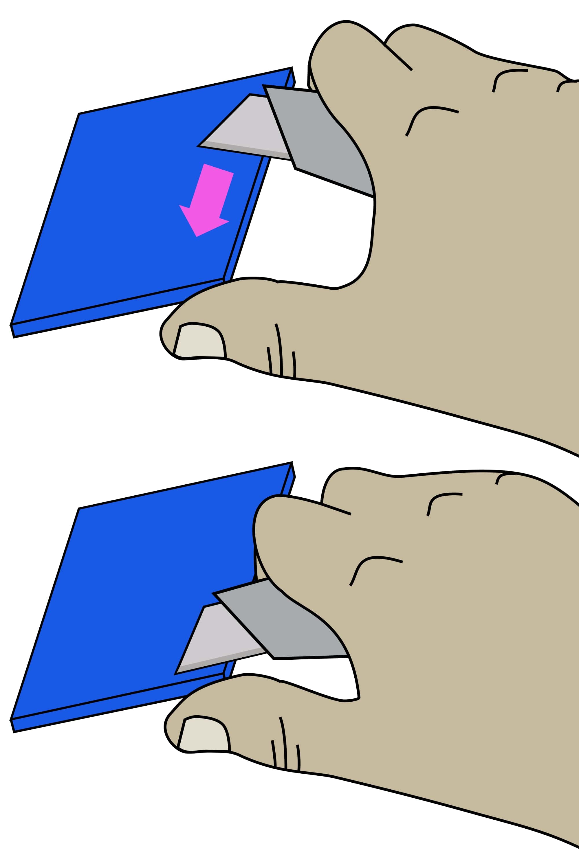
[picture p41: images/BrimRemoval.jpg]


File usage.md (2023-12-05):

# Use your laser module

>i **Please Note:** This site is under construction.

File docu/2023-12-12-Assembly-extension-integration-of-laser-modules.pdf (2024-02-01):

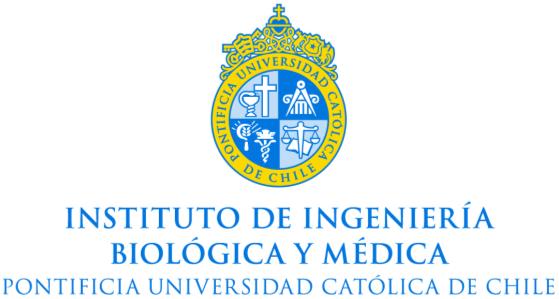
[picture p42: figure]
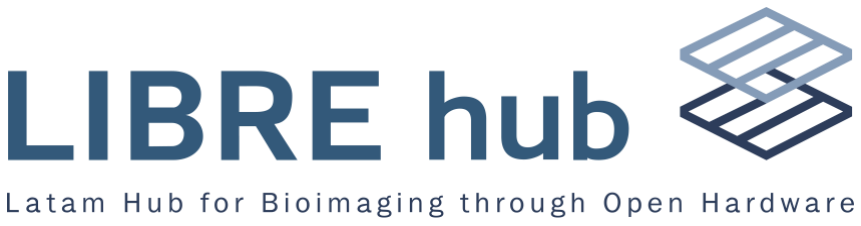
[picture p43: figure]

# Ensamblado, extensión e integración de módulos láser

Vicente Parot, PhD
vparot@uc.cl
Taller de iluminación láser de bajo costo

2023-12-12
10:00 – 13:00
14:00 – 15:00

## Taller LIBRE hub: Iluminación láser de bajo costo

- Clase 3B, puede causar daño en la retina
- Disminución de riesgo
− Luz horizontal a altura de la mesa
− Ojos nunca a la altura de la mesa
− Terminación del haz en una pantalla

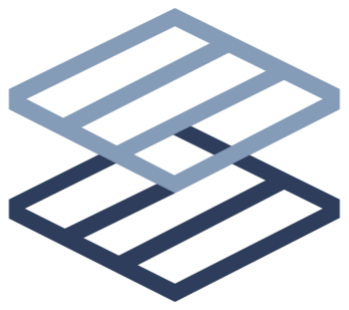
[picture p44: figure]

− Luz divergente o ensanchada a 10 mm, reduce cantidad de luz máxima que podría entrar al ojo
− Potencia limitada a 300 mW (violeta, rojo) y 100 mW (azul)
− Potencia regulada al mínimo posible
(aumentar sólo para pruebas controladas y breves)
- Letrero de seguridad
Vicente Parot - Taller LIBRE hub de iluminación láser | 2

# Configuración de alimentación de voltaje

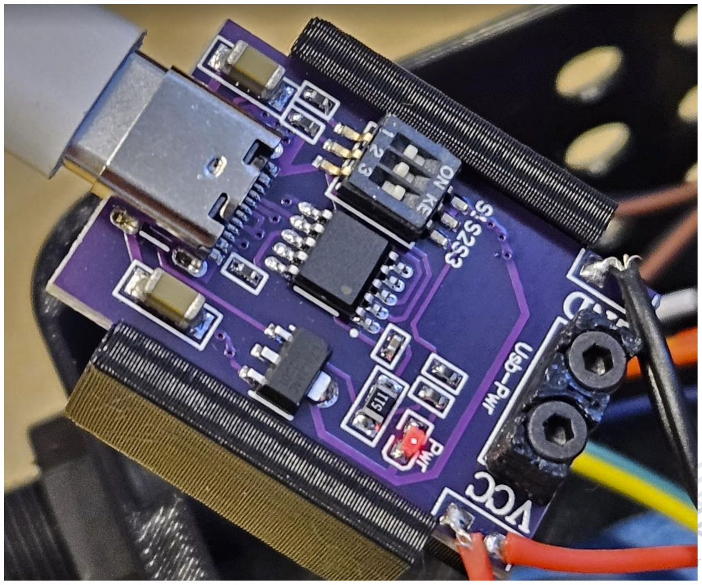
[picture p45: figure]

- Switch 1 OFF
- Switch 2 OFF
- Switch 3 ON

# Posicionamiento de lente colimador

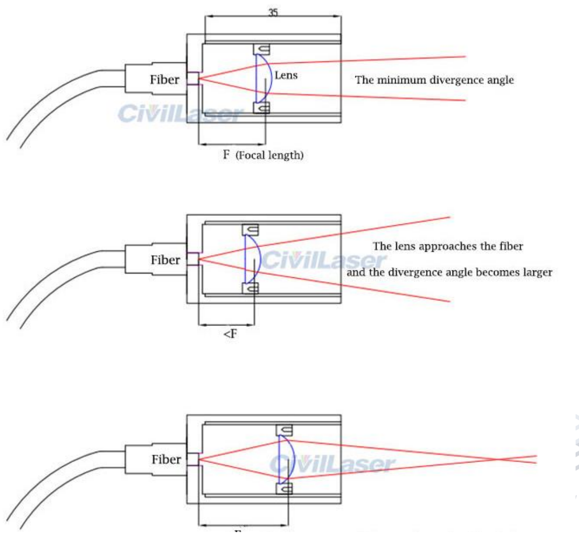
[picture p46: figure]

- Mínima divergencia
- Lente más cerca de la fibra → Aumenta la divergencia
- Lente más lejos de la fibra → Enfoque más cerca

# Posicionamiento de lente colimador

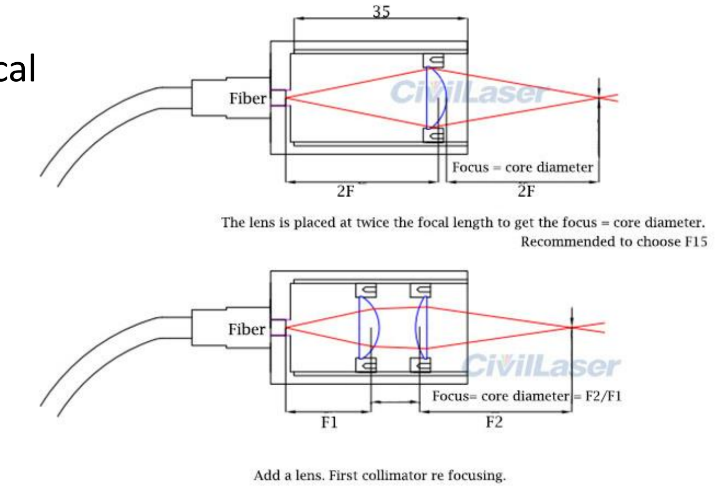
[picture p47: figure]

- Lente al doble de la distancia focal
→ Imagen del núcleo 1:1
- Dos lentes de distancias F1 y F2 → Magnificación F2/F1

# El patron proyectado varía con la distancia

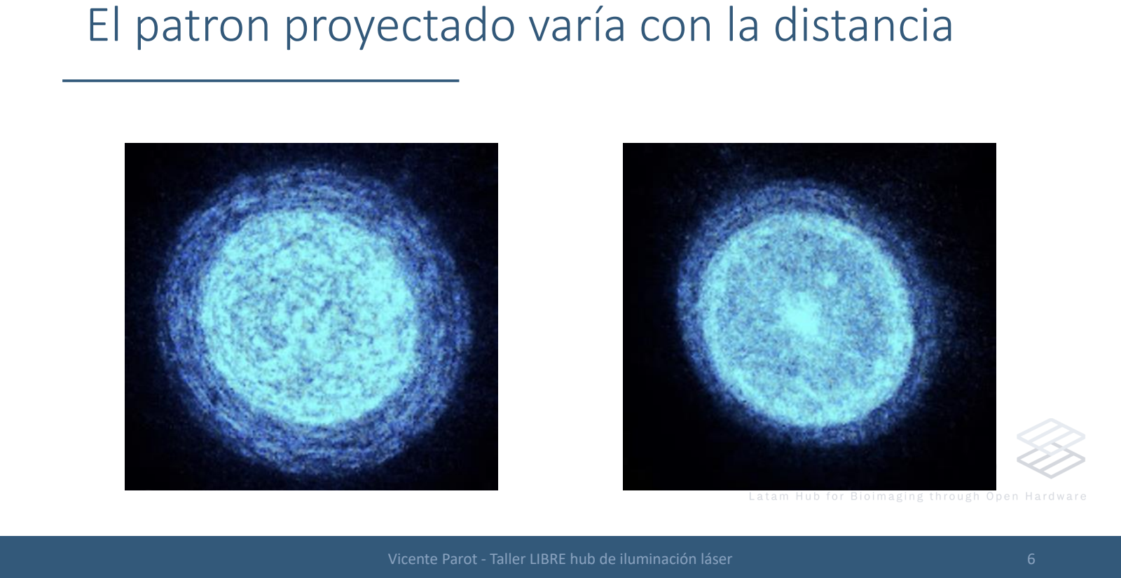
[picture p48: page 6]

# Caracterización de diodos láser

Especificado | Medido
Color | Corriente máxima | Operación normal | Operación normal | Operación máxima
405 nm | 400 mA | 300 mW @ 325 mA | 277 mW @ 320 mA | 312 mW @ 345 mA
488 nm | 135 mA | 55 mW @ 105 mA | 57.2 mW @ 100 mA | 84.7 mW @ 140 mA
638 nm | 1000 mA | 700 mW @ 970 mA | | 295 mW @ 460 mA
- Mediciones realizadas después de 10 min de encender el laser,
en módulos del taller, incluyendo limitación de corriente.
- Potencia óptica fue registrada con un medidor PM400 (https://www.thorlabs.com/thorproduct.cfm?partnumber=PM400) + S121C. (https://www.thorlabs.com/thorproduct.cfm?partnumber=S121C)

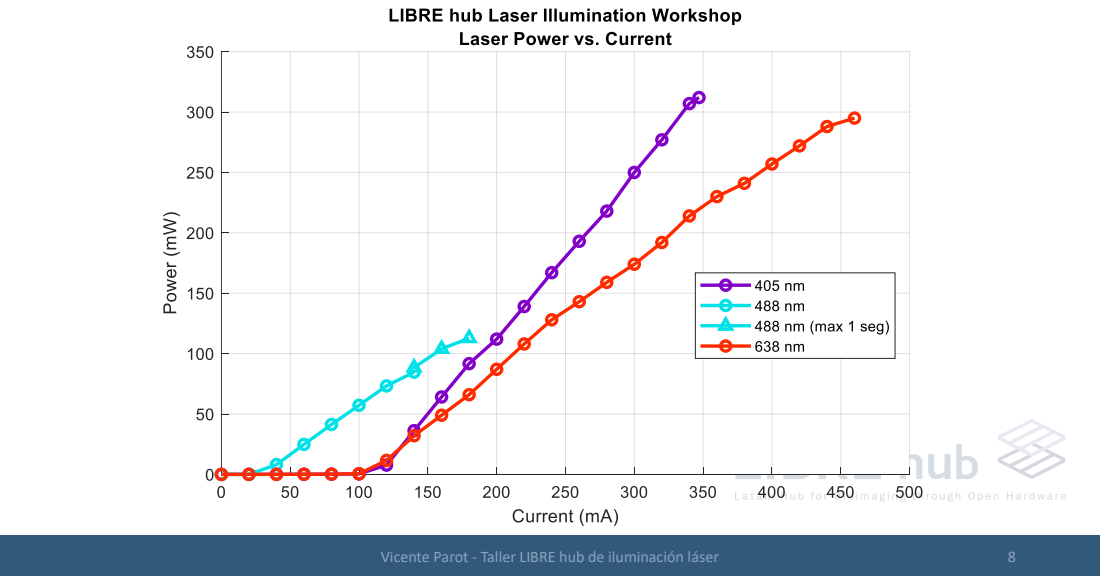
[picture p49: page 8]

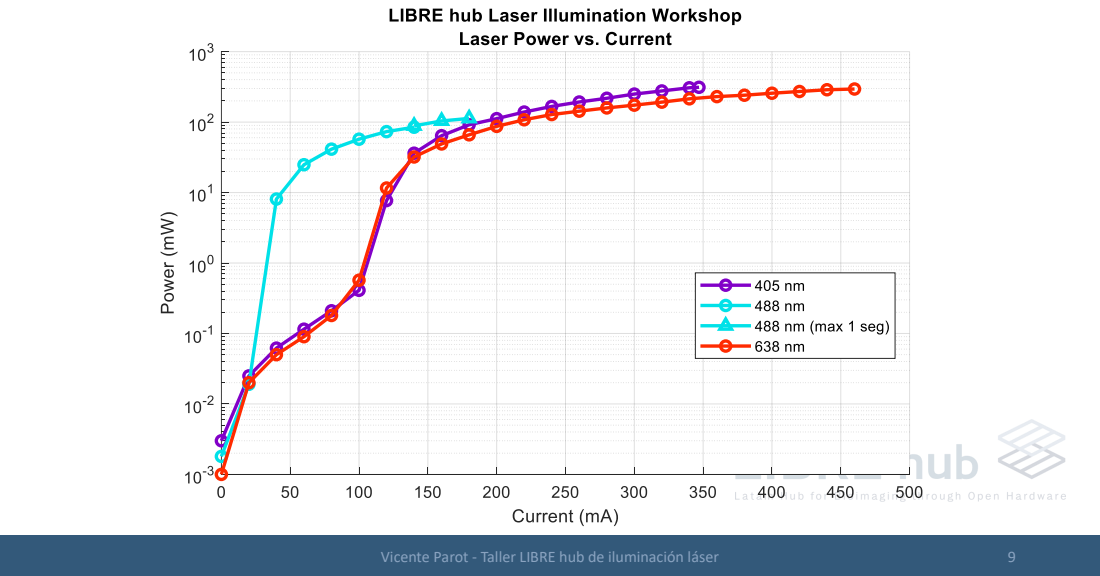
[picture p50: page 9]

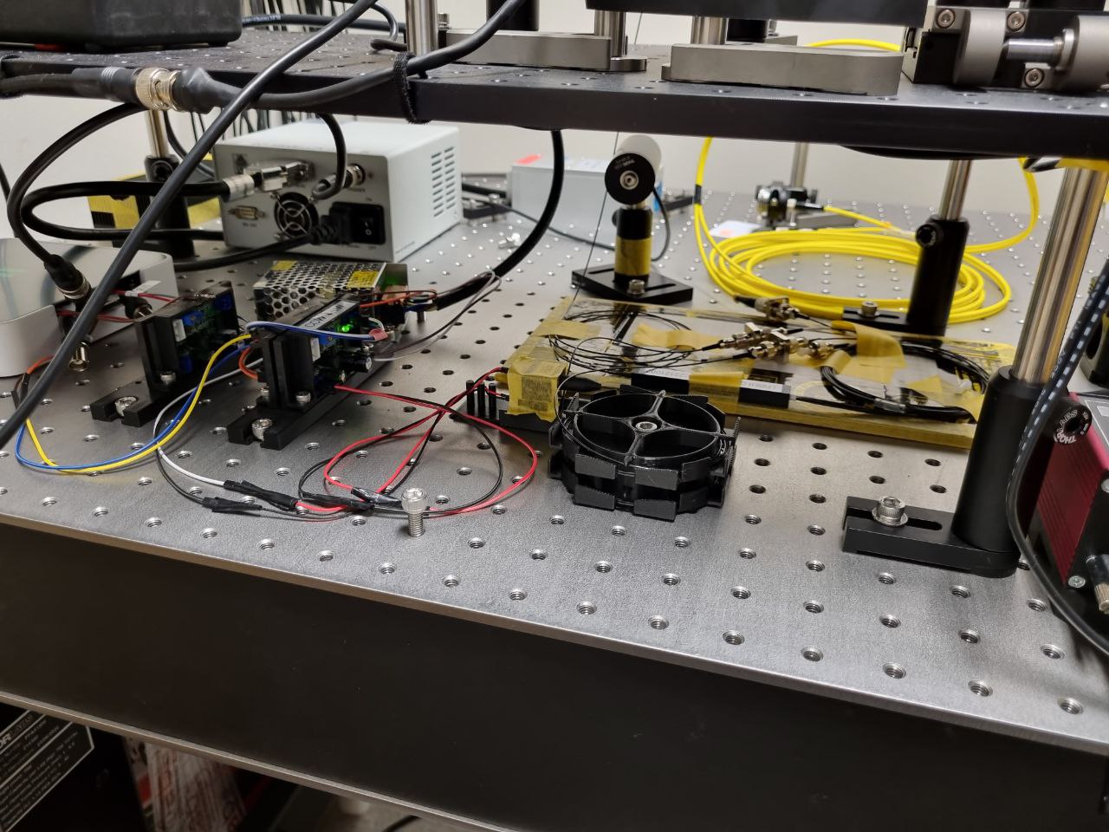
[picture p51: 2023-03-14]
Images-VP/montage.jpg

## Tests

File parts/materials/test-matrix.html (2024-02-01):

# Low-cost, modular fiber-coupled laser illumination

by Francisco Martinez, Matías Hurtado-Labarca, Pierre Padilla-Huamantinco, and Vicente Parot

Latin American Hub for Bioimaging Through Open Hardware (LIBRE hub)

# Test Matrix

Download test-matrix.pdf

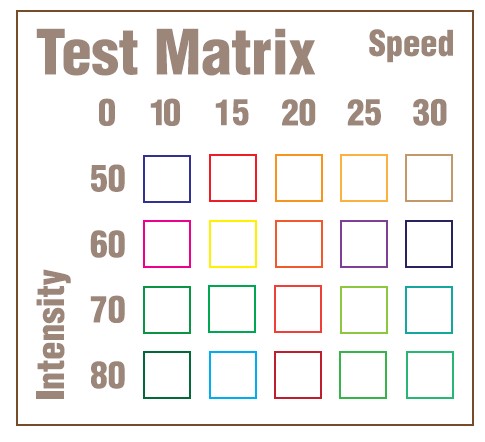
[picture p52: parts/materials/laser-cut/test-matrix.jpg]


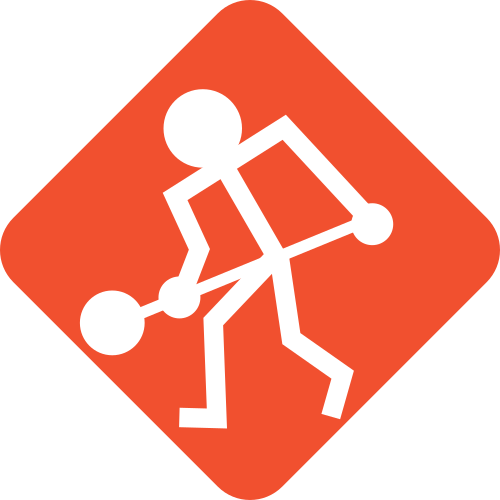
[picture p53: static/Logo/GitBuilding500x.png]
GitBuilding logo
 Documentation powered by GitBuilding (https://gitbuilding.io)

©2024 Francisco Martinez, Matías Hurtado-Labarca, Pierre Padilla-Huamantinco, and Vicente Parot

Contact: librehub@uc.cl

Low-cost, modular fiber-coupled laser illumination is released under CERN-OHL-W-2.0.

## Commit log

2023-12-05 Create GitBuilding documentation
    [leg_test.stl]
2023-12-05 Deploying to workshop-doc from @ d56cd808f650070aec15aafaccb9ef63ec1b39b3 🚀
    [assembly_BOM.csv]
2023-12-05 Deploying to workshop-doc from @ b5f118af3c25445a446780b4cab710bd60712b15 🚀
2023-12-05 Update laser cutting parameters
2023-12-05 Deploying to workshop-doc from @ 28224d6e529b60bda2c073cc631b3dbf4aaaa19e 🚀
2023-12-08 Deploying to workshop-doc from @ 91beb89dee2c3b347e2f77d32345295e01e089c2 🚀
    [assembly_BOM.csv]
2023-12-11 Deploying to workshop-doc from @ 47012e44520c018152de6f8f2dabb856e6d8a302 🚀
    [assembly_BOM.csv]
2023-12-11 Update Módulo Control Temperatura
2023-12-11 Deploying to workshop-doc from @ 42eceaf44a7b7bab46cc1dd16ac9f0e5446b3591 🚀
2023-12-11 Deploying to workshop-doc from @ 09bdd2c7af5e43e0b9717997401ad737f2d4f93d 🚀
2023-12-11 Update assembly instructions formats
2023-12-11 Deploying to workshop-doc from @ 913d855c544931ea0fe7d2280b74c08e7b097c46 🚀
2024-01-04 Deploying to workshop-doc from @ ff5d0c9d9c6a4c2da3f8ab52e3a955fd381668b5 🚀
2024-01-04 Deploying to workshop-doc from @ 8b34929468facf1f78d1c0ec315259b6c09e00bb 🚀
    [AdapterM2.stl, Difusor.stl, Herramienta.stl, S1.stl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]
2024-01-11 Deploying to workshop-doc from @ 579b28773bbfda110d78969960f60d677dc967dc 🚀
2024-01-11 Deploying to workshop-doc from @ 34af94aba81b7f0d552d61781ebd48afecc281ac 🚀
2024-01-18 Deploying to workshop-doc from @ 0f3c694b5d8360009b0e01ff4c185b45945d2f12 🚀
2024-01-23 Deploying to workshop-doc from @ b948f85da25475e1ee48f81ea8ac2411387aa224 🚀
2024-01-24 Deploying to workshop-doc from @ 4dd863f8537868a554eb2f3e7620ef1f2a2e8067 🚀
    [Tubolente.stl, adaptadorfibra-TL.stl, anillo-TL.stl, difusor-TL.stl]
2024-01-24 Deploying to workshop-doc from @ 504d25b47c5ca3c0550e7b3df33ea10cac83d91e 🚀
2024-01-30 Deploying to workshop-doc from @ 8d36263114266afe977b0e758a6c8ca29973d23b 🚀
2024-01-31 Deploying to workshop-doc from @ d6e9f1fc0a44a1285f768b489de851d451f5749b 🚀
2024-01-31 Deploying to workshop-doc from @ 26e4b90e21e03fe1b38b7cf1f0afb630c059e95d 🚀
2024-02-01 Deploying to workshop-doc from @ ae11b64d70ea50730d7ae226d6a6a9d48ba919dc 🚀
2024-02-01 Deploying to workshop-doc from @ 92fe102070cfeb808b9c1bcd3486ae360a6e94ca 🚀
